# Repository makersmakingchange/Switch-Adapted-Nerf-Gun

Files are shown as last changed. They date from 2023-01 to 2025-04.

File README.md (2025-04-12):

# Switch Adapted Nerf Gun
The Switch Adapted Nerf Gun is designed to be a switch adapted toy for an older audience. The majority of switch adapted toys are designed for a younger audience, so this project aims to adapt a toy aimed at older children and make it switch accessible.

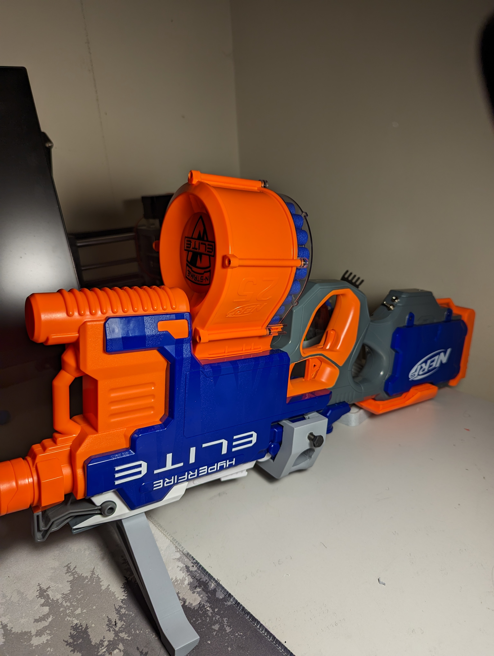
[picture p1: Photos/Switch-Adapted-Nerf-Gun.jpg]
Picture of Switch Adapted Nerf Gun.


## More info at
- [Makers Making Change Project Page](https://makersmakingchange.com/project/switch-adapted-nerf-gun/)

## How to Obtain a Switch Adapted Nerf Gun
### 1. Do it Yourself (DIY) or Do it Together (DIT)

This is an open-source assistive technology, so anyone is free to build it. All of the files and instructions required to build the Switch Adapted Nerf Gun are contained within this repository. Refer to the Maker Checklist below.

### 2. Request a build of this device

If you would like to obtain a Switch Adapted Nerf Gun, you may submit a build request through the [MMC Library Page](https://makersmakingchange.com/project/switch-adapted-nerf-gun/). The requestor is responsible for the cost of materials and any shipping.

### 3. How to build this device for someone else

If you have the skills and equipment to build this device, and would like to donate your time to create the switch for someone who needs it, visit the [MMC Maker Wanted](https://makersmakingchange.com/maker-wanted/) section.

## Getting Started

### 1. Read the Makers Checklist

The Makers Checklist contains a list of tasks to complete to build the device.
[The Makers Checklist](/Documentation/Switch_Adapted_Nerf_Gun_Maker_Checklist_V1.0.pdf)

### 2. Order the Off-The-Shelf Components

The [Bill of Materials](/Documentation/Switch_Adapted_Nerf_Gun_BOM_V1.0.xlsx) lists all of the parts and components required to build the Switch Adapted Nerf Gun. The main gun component needs to be ordered online. The rest of the off-the-shelf components are also online or may be available in smaller quantities at your local hardware store or dollar store.

### 3. Print the 3D Printable components

All of the files and individual print files can be in the [/Build_Files/3D_Printing_Files](/Build_Files/3D_Printing_Files/) folder.

### 4. Assemble the Switch Adapted Nerf Gun

Reference the [Assembly Guide](/Documentation/Switch_Adapted_Nerf_Gun_Assembly_Guide_V1.0.pdf) for the tools and steps required to build each portion.

## Files
### Documentation
| Document             | Version | Link |
|----------------------|---------|------|
| Design Rationale     | 1.0     | [Switch_Adapted_Nerf_Gun_Design_Rationale](/Documentation/Switch_Adapted_Nerf_Gun_Design_Rationale_V1.0.pdf)     |
| Maker Checklist      | 1.0     | [Switch_Adapted_Nerf_Gun_Maker_Checklist](/Documentation/Switch_Adapted_Nerf_Gun_Maker_Checklist_V1.0.pdf)     |
| Bill of Materials    | 1.0     | [Switch_Adapted_Nerf_Gun_Bill_of_Materials](/Documentation/Switch_Adapted_Nerf_Gun_BOM_V1.0.xlsx)     |
| 3D Printing Guide    | 1.0     | [Switch_Adapted_Nerf_Gun_3D_Printing_Guide](/Documentation/Switch_Adapted_Nerf_Gun_3D_Printing_Guide_V1.0.pdf)     |
| Assembly Guide       | 1.0     | [Switch_Adapted_Nerf_Gun_Assembly_Guide](/Documentation/Switch_Adapted_Nerf_Gun_Assembly_Guide_V1.0.pdf)     |
| User Guide           | 1.0     | [Switch_Adapted_Nerf_Gun_User_Guide](/Documentation/Switch_Adapted_Nerf_Gun_User_Guide_V1.0.pdf)    |
| Changelog            | 1.0     | [Switch_Adapted_Nerf_Gun_Changelog](/Documentation/Switch_Adapted_Nerf_Gun_Changelog_V1.0.pdf)     |

### Design Files
[CAD Files](/Design_Files/CAD_Files)

### Build Files
 - [3D Printing Files](/Build_Files/3D_Printing_Files)

## Attribution
Designers:
 - Design by [Nicholas Stallings](https://www.youtube.com/watch?v=sFg3B8Z95hU)
 - Documentation by Neil Squire Society/Makers Making Change

## License
Everything needed or used to design, make, test, or prepare the Switch Adapted Nerf Gun is licensed under the [Attribution-NonCommercial-ShareAlike 4.0 ](https://creativecommons.org/licenses/by-nc-sa/4.0/).

Accompanying material such as instruction manuals, videos, and other copyrightable works that are useful but not necessary to design, make, test, or prepare the <Device-Name> are published under a Creative Commons Attribution-ShareAlike 4.0 license https://creativecommons.org/licenses/by-sa/4.0/ (CC BY-SA 4.0).

---
<!-- ABOUT MMC START -->
## About Makers Making Change
[Makers Making Change Logo](https://www.makersmakingchange.com/)

Makers Making Change is a program of [Neil Squire](https://www.neilsquire.ca/), a Canadian non-profit that uses technology, knowledge, and passion to empower people with disabilities.

Makers Making Change leverages the capacity of community based Makers, Disability Professionals and Volunteers to develop and deliver affordable Open Source Assistive Technologies.

 - Website: [www.MakersMakingChange.com](https://www.makersmakingchange.com/)
 - GitHub: [makersmakingchange](https://github.com/makersmakingchange)
 - Bluesky: [@makersmakingchange.bsky.social](https://bsky.app/profile/makersmakingchange.bsky.social)
 - Instagram: [@makersmakingchange](https://www.instagram.com/makersmakingchange)
 - Facebook: [makersmakechange](https://www.facebook.com/makersmakechange)
 - LinkedIn: [Neil Squire Society](https://www.linkedin.com/company/neil-squire-society/)
 - Thingiverse: [makersmakingchange](https://www.thingiverse.com/makersmakingchange/about)
 - Printables: [MakersMakingChange](https://www.printables.com/@MakersMakingChange)

### Contact Us
For technical questions, to get involved, or to share your experience we encourage you to [visit our website](https://www.makersmakingchange.com/) or [contact us](https://www.makersmakingchange.com/s/contact).
<!-- ABOUT MMC END -->

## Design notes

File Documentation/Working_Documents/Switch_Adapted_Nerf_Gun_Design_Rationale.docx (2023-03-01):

# Introduction

The Switch Adapted Nerf Gun is designed to be a switch adapted toy for an older audience. The majority of switch adapted toys are designed for a younger audience, so this project aims to adapt a toy aimed at older users and make it switch accessible.

# Research

Commercial
Name | Image | Price | Link

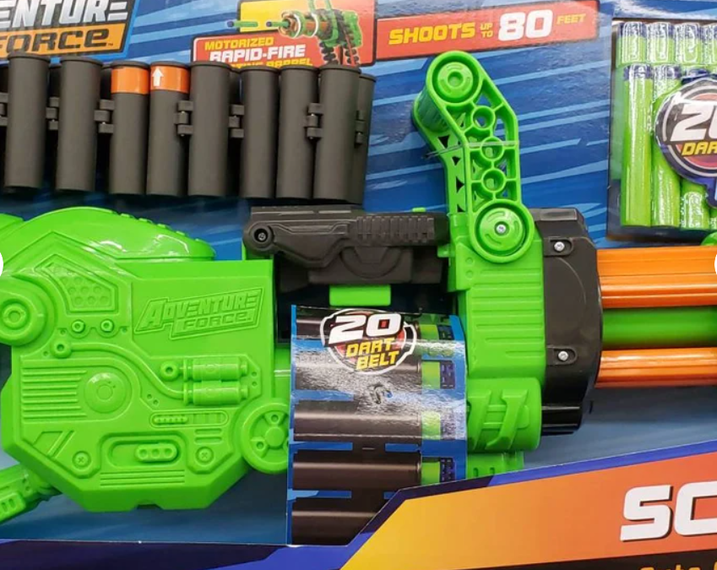
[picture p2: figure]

Switch Adapted modified Dart Blaster. For special needs. | | $99.74 | Link (https://www.etsy.com/ca/listing/648802112/switch-adapted-modified-dart-blaster-for)

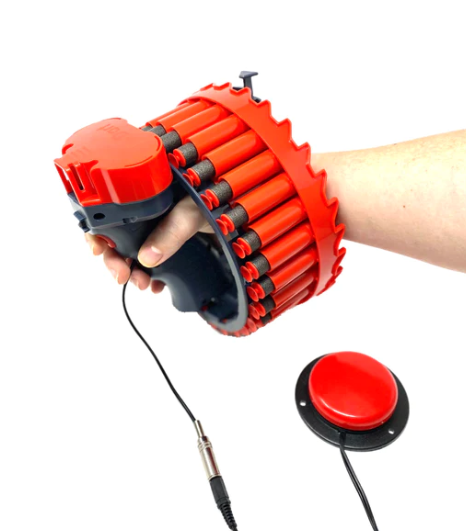
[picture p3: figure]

Dart Gun – Switch Adapted | | $70 | Link (https://adaptabilities.net/en-ca/products/switch-adapted-dart-gun-assistive-technology-toy-for-special-needs-education-occupational-physical-and-speech-therapy)

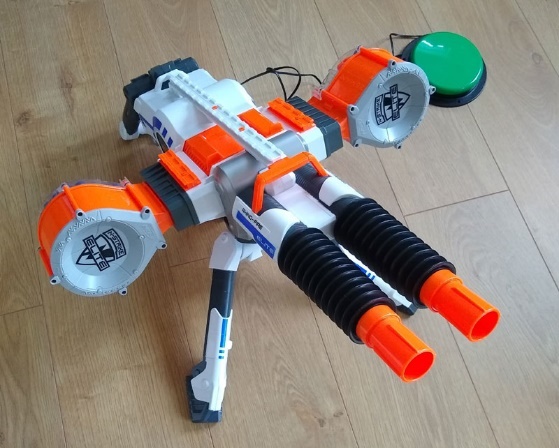
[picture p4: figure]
NERF Rhino switch adapted large plastic double-barrelled toy sentry gun.

Switch Adapted NERF Rhino-Fire Elite foam dart gun | | Price available upon email request | Link (https://oneswitch.org.uk/page/shop-switch-adapted-nerf-foam-dart-gun)

DIY
Name | Image | Price | Link

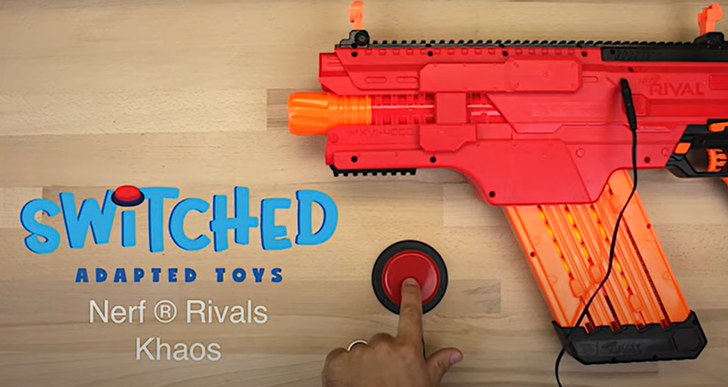
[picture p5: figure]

SWITCHED Adapted Toys - Nerf Rivals Khaos - Manual | | Unavailable | Link (https://www.switchedtoys.org/adapt-attack)

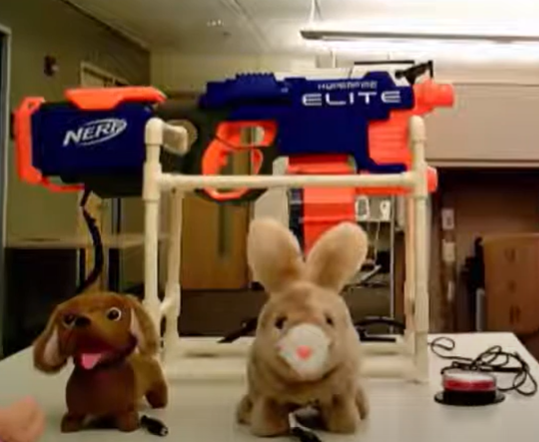
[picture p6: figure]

IATP- Switch adapted Nerf gun | | Unavailable | Link (https://www.youtube.com/watch?v=AM-woh1qSKs)

# Requirements

## Goals

G01 | Allow a Nerf gun to be operated by an accessible switch

## Functional Requirements

F01 | Add a mono jack to allow the primary user to control the feed motor
F02 | Add a toggle switch to allow the secondary user to toggle the flywheel motor
F03 | Add a stand that allows the gun to standalone on a surface and be mounted on a ¼-20 UNC system

## Non-functional Requirement

NF01 | Add a second mono jack to allow the primary user to operate the flywheel motor.

## Constraints

C01 | Design must still allow the gun to be used normally

# Prototyping

When opening the gun, the circuit was found to be different from the circuit in the gun in the tutorial video. Minor changes to the procedure had to be made to adapt the feed motor trigger. The initial circuit diagram can be seen on the left, while the modified circuit diagram is on the right.

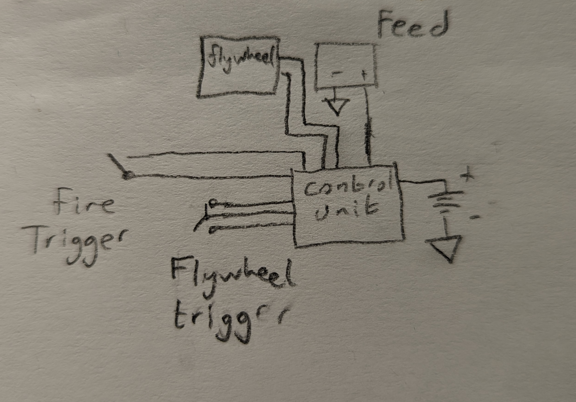
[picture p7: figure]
Original circuit diragram
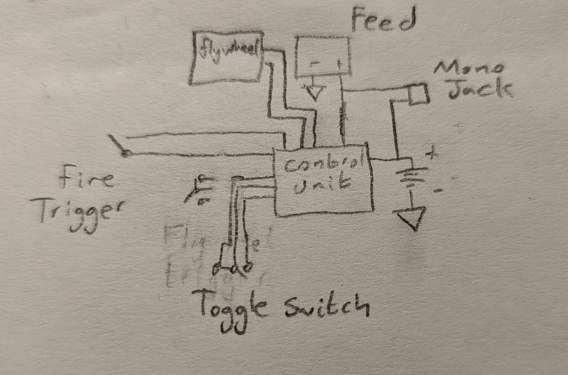
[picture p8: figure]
Modified circuit diagram

Two stands were designed for the gun. One bipod style desk stand was designed to fit over the attachment rail and allow the gun to stand upside down on a flat surface, while a ¼-20 bolt stand was developed that attaches to the gun near the centre of gravity and allows the gun to be attached to a standard ¼-20 mounting system.

# Testing

The successfully adapted toy was tested with a standard 3.5 mm switch using both the desk stand and the ¼-20 bolt stand. The gun was able to stand and support itself firing with both stands.

# Opportunities for Improvement

Once the control circuit is better understood, a 3.5 mm jack can be put in parallel with the toggle switch to make the flywheel motor usable by the primary user.

A system could be constructed to trigger both motors on the same switch, with a roughly one second delay on the feed motor to allow the firing motor to get up to speed.

© 2022 by Neil Squire. This work is licensed under the CC BY SA 4.0 License: http://creativecommons.org/licenses/by-sa/4.0 Files available at https://makersmakingchange.com/project/switch-adapted-nerf-gun/ Page 10 of 10

V1.0 | January 2023 Switch Adapted Nerf Gun Design Rationale

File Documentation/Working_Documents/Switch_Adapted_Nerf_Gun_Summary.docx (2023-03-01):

# Title

Switch Adapted Nerf Gun

## Subtitle

A Nerf Hyperfire Elite gun that has been adapted for use with a 3.5mm mono switch

## Device Details

### Overview

The Switch Adapted Nerf Gun is designed to be a switch adapted toy for an older audience. The majority of switch adapted toys are designed for a younger audience, so this project aims to adapt a toy aimed at older users and make it switch accessible.

### Usage

To set up the Nerf gun on a flat surface, take the Desk stand and slide it onto the top attachment rail. This will allow the gun to stand by itself upside down.

To set up the Nerf gun on a ¼-20 bolt system, take the bolt stand and attach it to the section of the gun above the trigger as seen in the assembly guide. This will allow the gun to be attached to any ¼-20 mount system.

To use the gun, a 3.5mm switch can be plugged into the jack, and a secondary user can flick the toggle switch to activate the flywheel motors. Once the motors are spinning, the switch can be pressed and held to activate the feed motor for as long as the button is held.

### Cost

~$95 total

~$75 toy

~$20 dollars batteries and adaptation

### Build Instructions

The build involves opening the nerf gun to modify two switches that will allow the gun to be fired with a 3.5mm mono switch.

#### Skills Required

- Soldering
- 3D printing

#### Time Required

3D Printing:

8h38min

Assembly:

1h30min

#### Tools

Soldering Iron

Screwdriver

Wire Strippers

Drill with 1/4inch drill bit

#### Components

- Nerf Hyperfire Elite
- D-Cell Batteries
- ¼ -20 T-Slot Nut
- ¼-20 Bolts

#### 3D Printing

- Desk Stand
- Bolt Stand

### Attribution

- Switch adaptation design by Nicholas Stallings (https://www.youtube.com/watch?v=sFg3B8Z95hU)
- Mounting options design by Neil Squire Society/Makers Making Change
- Documentation by Neil Squire Society/Makers Making Change

© 2022 by Neil Squire. This work is licensed under the CC BY SA 4.0 License: http://creativecommons.org/licenses/by-sa/4.0 Files available at https://makersmakingchange.com/project/switch-adapted-nerf-gun/ Page 10 of 10

V1.0 | January 2023 Switch Adapted Nerf Gun Summary

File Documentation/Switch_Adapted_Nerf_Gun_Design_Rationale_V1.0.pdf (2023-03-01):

V1.0 | January 2023

## Switch Adapted Nerf Gun

## DESIGN RATIONALE

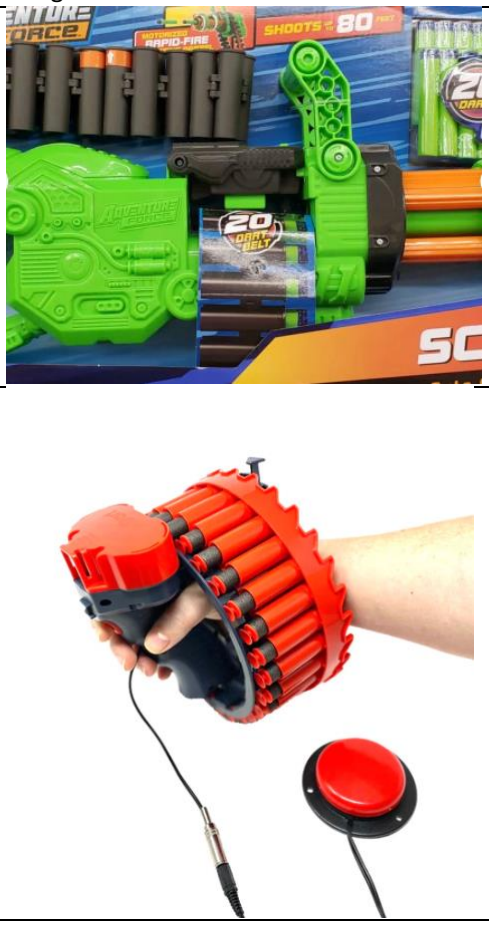
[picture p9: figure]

© 2022 by Neil Squire. (https://neilsquire.ca/)
This work is licensed under the CC BY SA 4.0 License: http://creativecommons.org/licenses/by-sa/4.0
Files available at https://makersmakingchange.com/project/switch-adapted-nerf-gun/ | Page 1 of 4

### Introduction

The Switch Adapted Nerf Gun is designed to be a switch adapted toy for an older audience. The majority of switch adapted toys are designed for a younger audience, so this project aims to adapt a toy aimed at older users and make it switch accessible.

### Research

Commercial
Name | Image | Price | Link
Switch Adapted modified Dart Blaster. For special needs. | | $99.74 | Link (https://www.etsy.com/ca/listing/648802112/switch-adapted-modified-dart-blaster-for)
Dart Gun – Switch Adapted | | $70 | Link (https://adaptabilities.net/en-ca/products/switch-adapted-dart-gun-assistive-technology-toy-for-special-needs-education-occupational-physical-and-speech-therapy)

## DESIGN RATIONALE

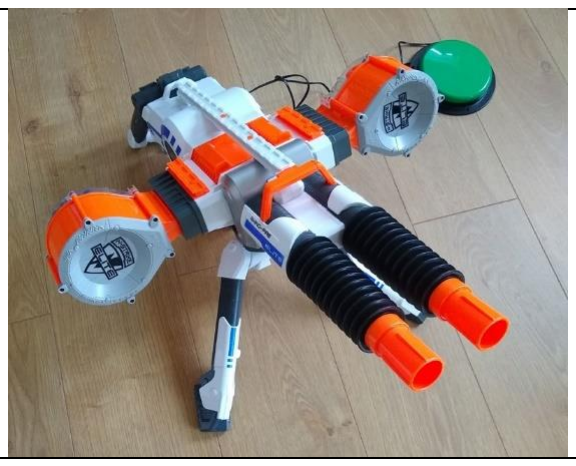
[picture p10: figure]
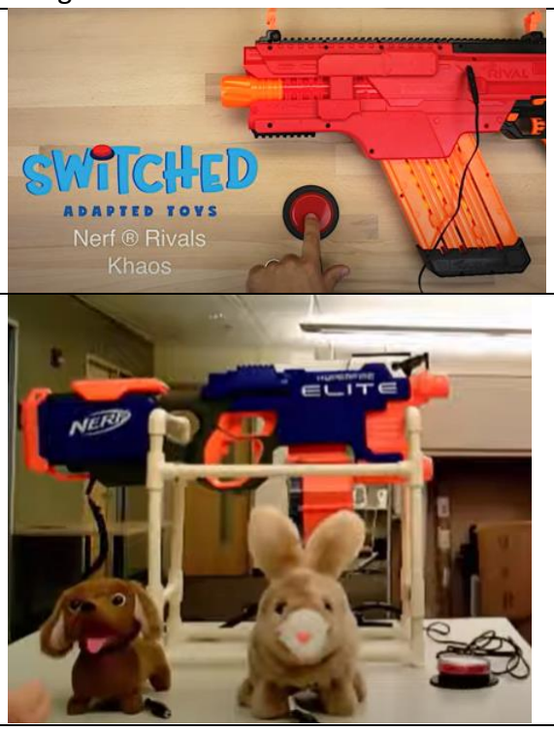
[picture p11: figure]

Files available at https://makersmakingchange.com/project/switch-adapted-nerf-gun/ | Page 2 of 4

Switch
Adapted NERF
Rhino-Fire Elite
foam dart gun

Price available
upon email
request

Link (https://oneswitch.org.uk/page/shop-switch-adapted-nerf-foam-dart-gun)

DIY
Name | Image | Price | Link
SWITCHED Adapted Toys -Nerf Rivals Khaos -Manual | | Unavailable | Link (https://www.switchedtoys.org/adapt-attack)
IATP- Switch adapted Nerf gun | | Unavailable | Link (https://www.youtube.com/watch?v=AM-woh1qSKs)

### Requirements

### Goals

G01 Allow a Nerf gun to be operated by an accessible switch

### Functional Requirements

F01 | Add a mono jack to allow the primary user to control the feed motor
F02 | Add a toggle switch to allow the secondary user to toggle the flywheel motor
F03 | Add a stand that allows the gun to standalone on a surface and be mounted on a ¼-20 UNC system

## DESIGN RATIONALE

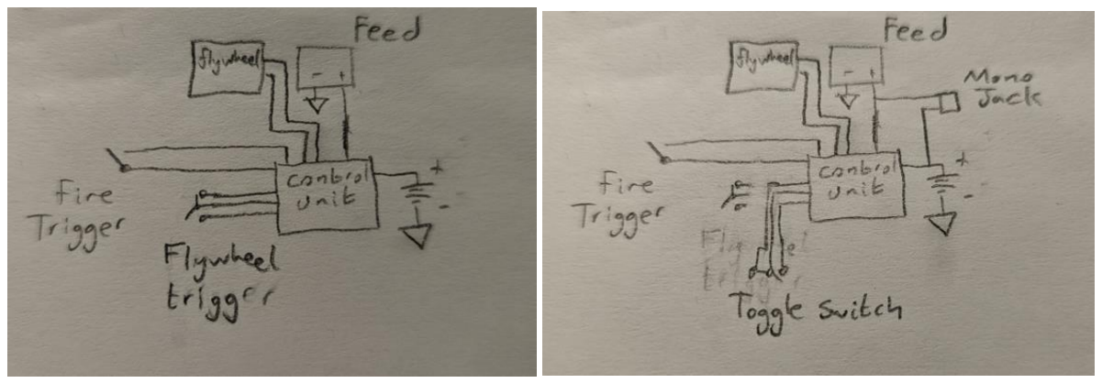
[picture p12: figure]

Files available at https://makersmakingchange.com/project/switch-adapted-nerf-gun/ | Page 3 of 4

### Non-functional Requirement

NF01 Add a second mono jack to allow the primary user to operate the flywheel motor.

### Constraints

C01 Design must still allow the gun to be used normally

### Prototyping

When opening the gun, the circuit was found to be different from the circuit in the gun in the tutorial video. Minor changes to the procedure had to be made to adapt the feed motor trigger. The initial circuit diagram can be seen on the left, while the modified circuit diagram is on the right.

Two stands were designed for the gun. One bipod style desk stand was designed to fit over the attachment rail and allow the gun to stand upside down on a flat surface, while a ¼-20 bolt stand was developed that attaches to the gun near the centre of gravity and allows the gun to be attached to a standard ¼-20 mounting system.

### Testing

The successfully adapted toy was tested with a standard 3.5 mm switch using both the desk stand and the ¼-20 bolt stand. The gun was able to stand and support itself firing with both stands.

### Opportunities for Improvement

Once the control circuit is better understood, a 3.5 mm jack can be put in parallel with the toggle switch to make the flywheel motor usable by the primary user.

## DESIGN RATIONALE

Files available at https://makersmakingchange.com/project/switch-adapted-nerf-gun/ | Page 4 of 4

A system could be constructed to trigger both motors on the same switch, with a roughly one second delay on the feed motor to allow the firing motor to get up to speed.

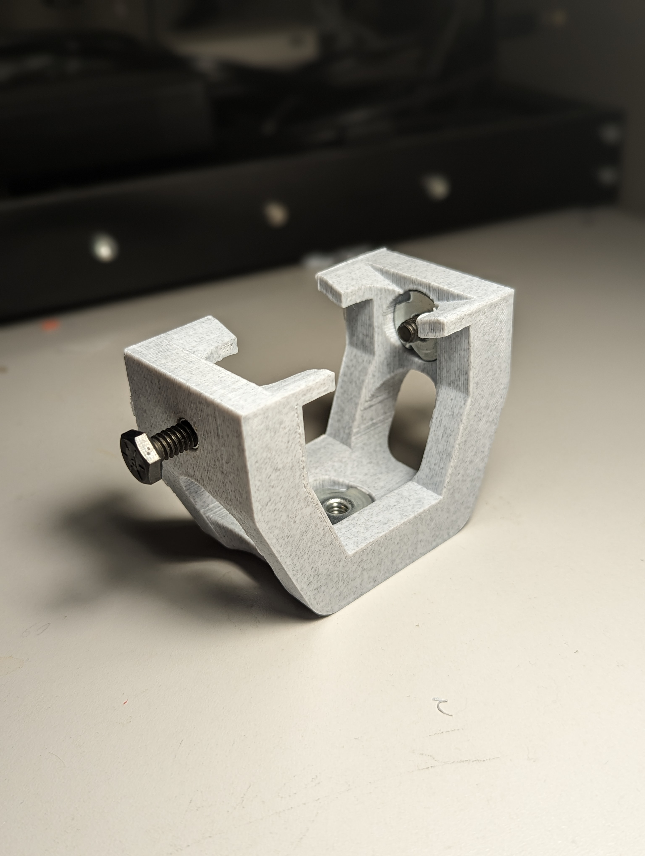
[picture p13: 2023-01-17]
Photos/PXL_20230106_003917938.PORTRAIT.jpg

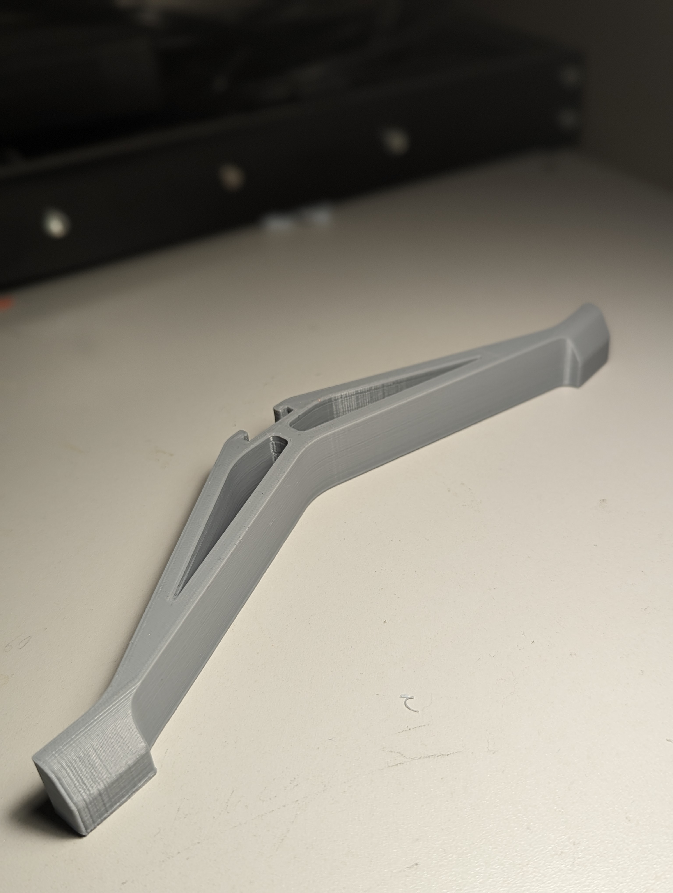
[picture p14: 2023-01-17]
Photos/PXL_20230106_003909670.PORTRAIT.jpg

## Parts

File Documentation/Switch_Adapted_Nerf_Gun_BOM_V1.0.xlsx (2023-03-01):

Device: Switch Adapted Nerf Gun |  | Total Cost | Total Print time (hr) | Total filament (g)
Version: V1.0 | Date Created: 01/06/2023 | $91.19 | 8.63 | 64
Commercial Parts:
Part type (Electrical. Mechanical, Sanitization, ect) | Part Name | Quantity Needed | Pkg Quantity | Price per package | Price per Unit | Price for qty needed | Link
Mechanical | Nerf N-Strike Elite HyperFire Blaseter | 1 | 1 | $71.99 | $71.99 | $71.99 | https://www.amazon.ca/dp/B018KLHT5O
Electrical | D Cell Battery | 4 | 4 | $12.82 | $3.21 | $12.82 | https://www.amazon.ca/dp/B00000JHQC/
Mechanical | 1/4-20 T Nut | 3 | 100 | $14.40 | $0.14 | $0.43 | https://www.mcmaster.com/90975A309/
Mechanical | 1/4-20 Bolt | 2 | 25 | $17.99 | $0.72 | $1.44 | https://www.amazon.ca/dp/B097NWWQFC/
Electrical | Toggle Switch | 1 | 10 | $15.96 | $1.60 | $1.60 | https://www.amazon.ca/dp/B01BWL7Z44/ | https://www.aliexpress.com/item/1005001558947112.html
Electrical | Mono Jack | 1 | 10 | $13.09 | $1.31 | $1.31 | https://www.amazon.ca/dp/B07R9SV6F5/
3D Printed Parts ESTIMATED PRICING USING 1KG ROLL COST: | $25.00
Part | Description | Quantity Needed | TOTAL Mass (g) | Estimated Price | Print Time (Min) | Link
Desk Stand | Allows the gun to stand unsupported on a surface | 1 | 27 | $0.68 | 232
Bolt Stand | Allows the gun to be attacked to a 1/4-20 system | 1 | 37 | $0.92 | 286
 |  |  |  | $0.00
 |  |  |  | $0.00
 |  |  |  | $0.00
 |  |  | Total Print Cost: | $1.60
Tools for Assembly
Alternatives (if there are other sources for some parts link them below)
Part and description | Link

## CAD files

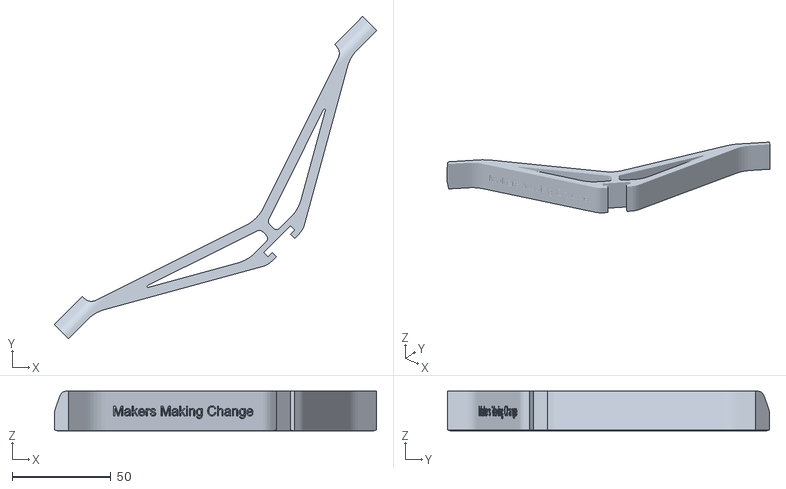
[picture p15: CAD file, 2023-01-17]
Build_Files/3D_Printing_Files/Desk_Stand.stl
162.6 x 162.6 x 20.0

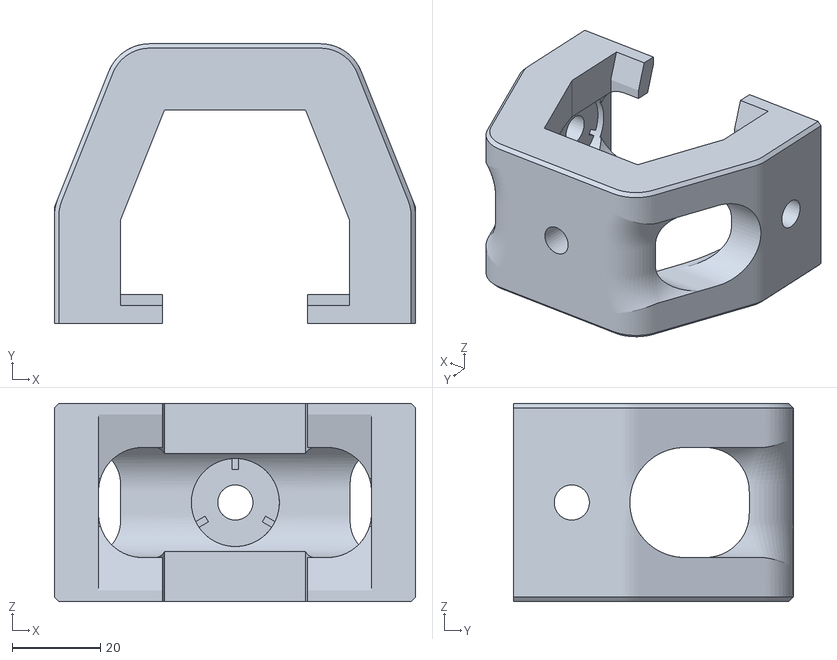
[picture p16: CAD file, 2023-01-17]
Build_Files/3D_Printing_Files/Bolt_Stand.stl
82.0 x 63.5 x 45.0

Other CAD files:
Design_Files/CAD_Files/Bolt Stand v6.f3d
Design_Files/CAD_Files/Stand v3.f3d

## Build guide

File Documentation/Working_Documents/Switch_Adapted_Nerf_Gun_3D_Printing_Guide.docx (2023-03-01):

# 3D Printing Summary

Metrics | Desk Stand | Bolt Stand
Total Print Time (min) | 232 | 286
Total Number of Components | 1 | 1
Typical Total Mass (g) | 27 | 37
Typical Number of Print Setups | 1 | 1

# 3D Printing Settings

Print File Name | Qty | Total Print Time (hr:min) | Mass (g) | Infill (%) | Support(Y/N) | Layer Height/ Nozzle Diameter(mm) | Notes (orientation, special settings, etc.)
Desk_Stand.stl | 1 | 3:52 | 27 | 20 | N | 0.2/0.4 | - Print in default stl orientation
Bolt_Stand.stl | 1 | 4:46 | 37 | 20 | N | 0.2/0.4 | - Print in default stl orientation

# Customization Options

- The device can be printed in any colour the user wants

# Post-Processing

- Use a hobby knife to remove any sharp edges.
- If using the bolt stand, insert ¼-20 t-nuts into the three slots in the Bolt stand as seen in the assembly guide.

# Examples of Quality Prints

Photos of Desk Stand

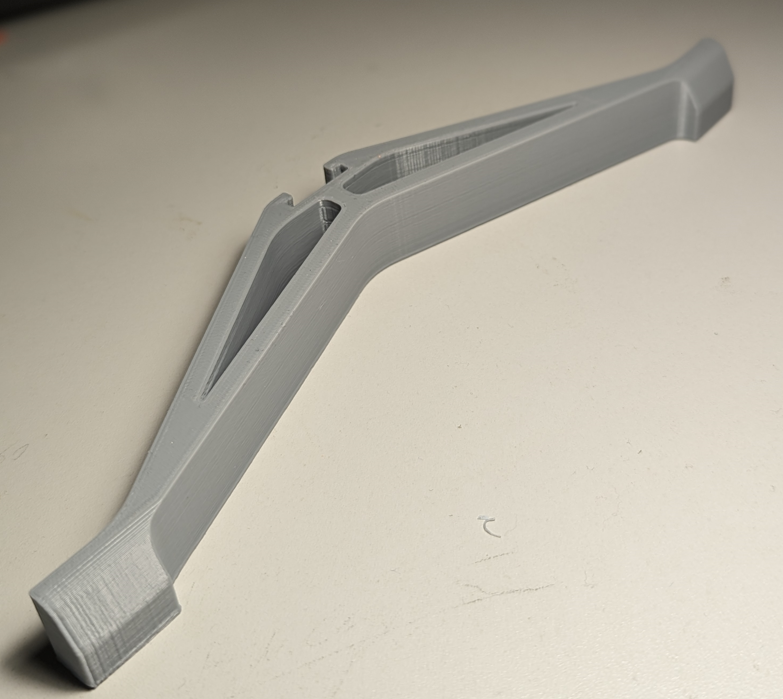
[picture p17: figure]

Photos of Bolt Stand

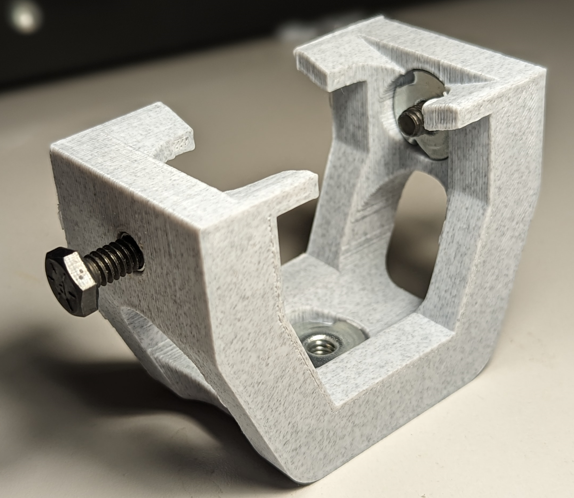
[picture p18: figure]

© 2022 by Neil Squire Society This work is licensed under the CC BY SA 4.0 License: http://creativecommons.org/licenses/by-sa/4.0 Files available at https://makersmakingchange.com/project/switch-adapted-nerf-gun/ Page 10 of 10

V1.0 | January 2023 Switch Adapted Nerf Gun 3D Printing Guide

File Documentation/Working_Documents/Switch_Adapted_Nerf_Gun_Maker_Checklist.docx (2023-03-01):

# Maker To Do List

- Read through the Assembly Guide to become familiar with required components, tools, supplies, and safety gear and overall assembly steps.
- Talk to User about customization options (e.g., color, any special requests, etc.)
- Order hardware components
- Gather tools, supplies, and safety equipment.
- Assemble the device
- Test device
- Print “User Quick Guide”

# Items to Give to User

- Assembled, tested device
- “User Quick Guide”

© 2022 by Neil Squire. This work is licensed under the CC BY SA 4.0 License: http://creativecommons.org/licenses/by-sa/4.0 Files available at https://makersmakingchange.com/project/switch-adapted-nerf-gun/ Page 10 of 10

V1.0 | January 2023 Switch Adapted Nerf Gun Maker Checklist

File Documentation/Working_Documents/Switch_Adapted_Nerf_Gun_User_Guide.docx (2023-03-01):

## Introduction

The Switch Adapted Nerf Gun is designed to be a switch adapted toy for an older audience. The majority of switch adapted toys are designed for a younger audience, so this project aims to adapt a toy aimed at older users and make it switch accessible.

## Features

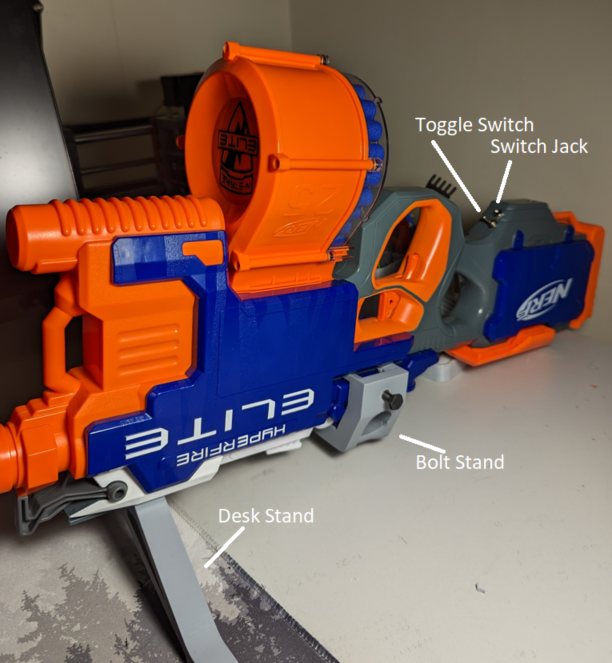
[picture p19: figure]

## Usage

To set up the Nerf gun on a flat surface, take the Desk stand and slide it onto the top attachment rail. This will allow the gun to stand by itself upside down.

To set up the Nerf gun on a ¼-20 bolt system, take the bolt stand and attach it to the section of the gun above the trigger as seen below. This will allow the gun to be attached to any ¼-20 mount system.

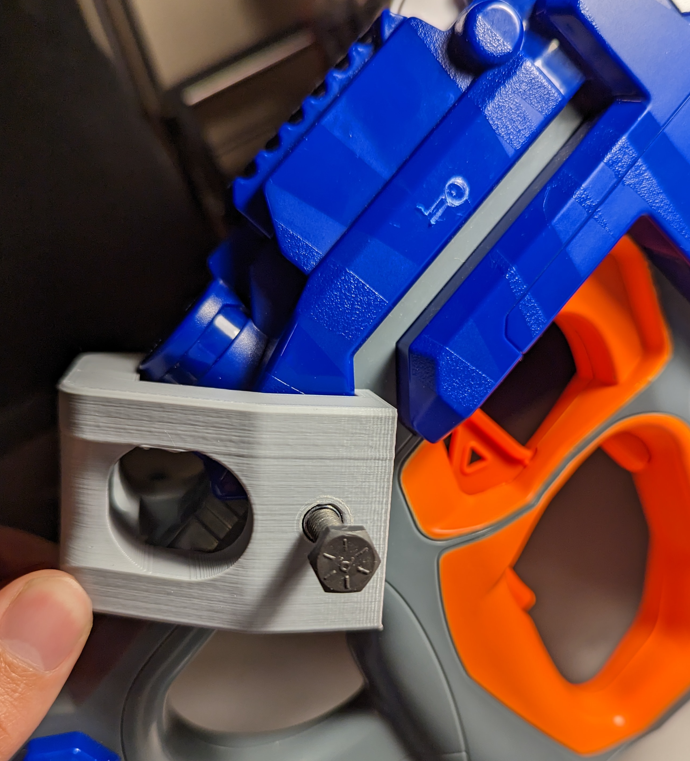
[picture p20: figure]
Bolt stand initially placed on gun
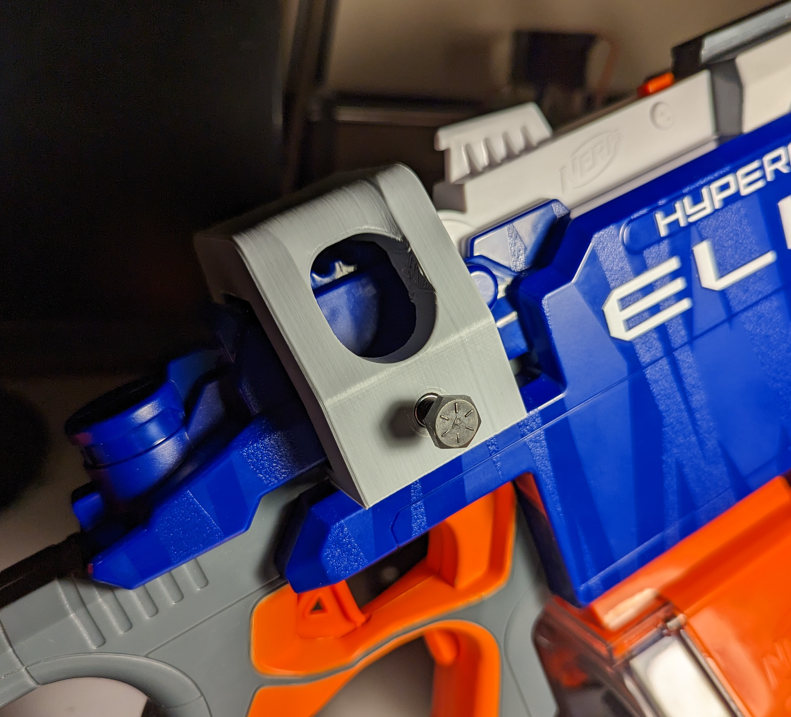
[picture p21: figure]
Bolt stand fully on gun

To use the gun, a 3.5mm switch can be plugged into the jack, and a secondary user can flick the toggle switch to activate the flywheel motors. Once the motors are spinning, the switch can be pressed and held to activate the feed motor for as long as the button is held.

## Compatibility

The device is compatible with standard 3.5mm switches as well as Nerf Elite darts.

## Cleaning

The device can be wiped clean with a damp cloth

© 2022 by Neil Squire. This work is licensed under the CC BY SA 4.0 License: http://creativecommons.org/licenses/by-sa/4.0 Files available at https://makersmakingchange.com/project/switch-adapted-nerf-gun/ Page 10 of 10

V1.0 | January 2023 Switch Adapted Nerf Gun user Quick Guide

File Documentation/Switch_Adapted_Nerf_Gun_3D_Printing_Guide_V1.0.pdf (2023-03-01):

V1.0 | January 2023

## Switch Adapted Nerf Gun

## 3D PRINTING GUIDE

© 2022 by Neil Squire Society This work is licensed under the CC BY SA 4.0 License: http://creativecommons.org/licenses/by-sa/4.0
Files available at https://makersmakingchange.com/project/switch-adapted-nerf-gun/ | Page 1 of 2

### 3D Printing Summary

Metrics | Desk Stand | Bolt Stand
Total Print Time (min) | 232 | 286
Total Number of Components | 1 | 1
Typical Total Mass (g) | 27 | 37
Typical Number of Print Setups | 1 | 1

### 3D Printing Settings

Print File Name | Qty | Total Print Time (hr:min) | Mass (g) | Infill (%) | Support(Y/N) | Layer Height/ Nozzle Diameter(mm) | Notes (orientation, special settings, etc.)
Desk_Stand.stl | 1 | 3:52 | 27 | 20 | N | 0.2/0.4 | -Print in default stl orientation
Bolt_Stand.stl | 1 | 4:46 | 37 | 20 | N | 0.2/0.4 | -Print in default stl orientation

### Customization Options

- The device can be printed in any colour the user wants

### Post-Processing

- Use a hobby knife to remove any sharp edges.
- If using the bolt stand, insert ¼-20 t-nuts into the three slots in the Bolt stand as seen in the assembly guide.

V1.0 | January 2023

## Switch Adapted Nerf Gun

## 3D PRINTING GUIDE

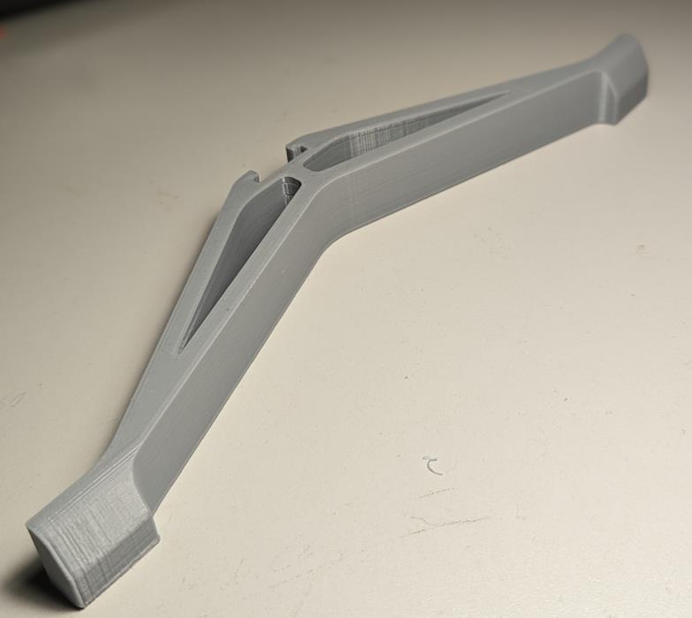
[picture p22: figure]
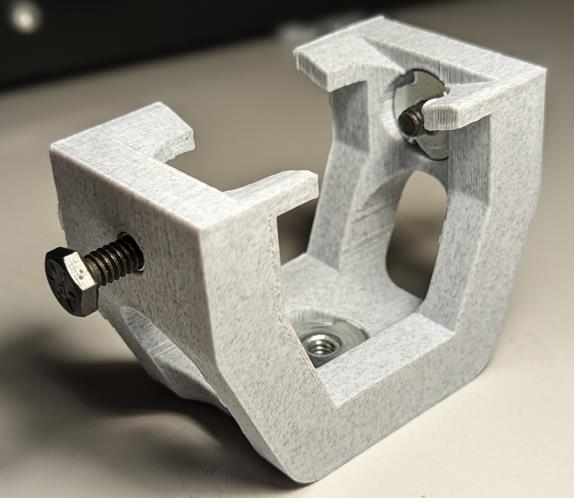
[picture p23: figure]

© 2022 by Neil Squire Society This work is licensed under the CC BY SA 4.0 License: http://creativecommons.org/licenses/by-sa/4.0
Files available at https://makersmakingchange.com/project/switch-adapted-nerf-gun/ | Page 2 of 2

### Examples of Quality Prints

Photos of Desk Stand

Photos of Bolt Stand

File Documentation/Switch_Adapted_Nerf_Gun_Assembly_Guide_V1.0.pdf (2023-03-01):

V1.0 | January 2023

# Switch Adapted Nerf Gun

# ASSEMBLY GUIDE

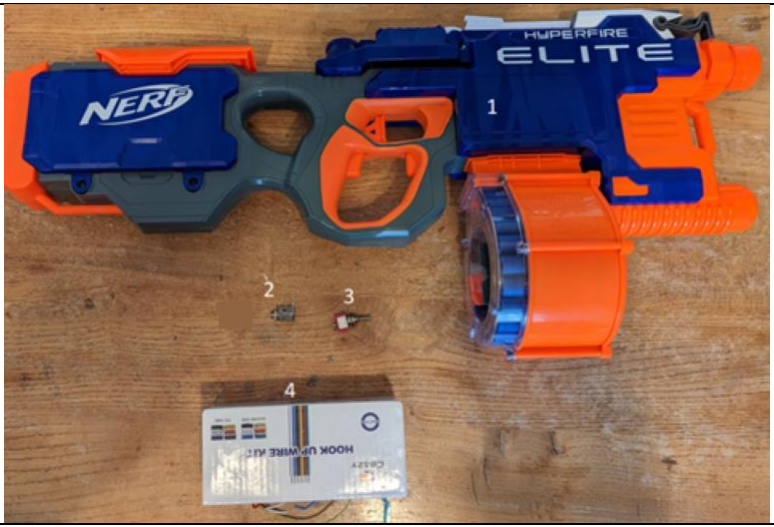
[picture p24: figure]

© 2022 by Neil Squire. (https://neilsquire.ca/)
This work is licensed under the CC BY SA 4.0 License: http://creativecommons.org/licenses/by-sa/4.0
Files available at https://makersmakingchange.com/project/switch-adapted-nerf-gun/ | Page 1 of 10

# Required Components

## BOM 1. 1x Nerf Hyperfire Elite 2. 1x Mono Jack 3. 1x Toggle Switch 4. Wire

# Required Tools

## - Soldering Iron - Solder - Electrical Tape - Wire Strippers - Screwdriver - Drill with ¼ inch bit

# ASSEMBLY GUIDE

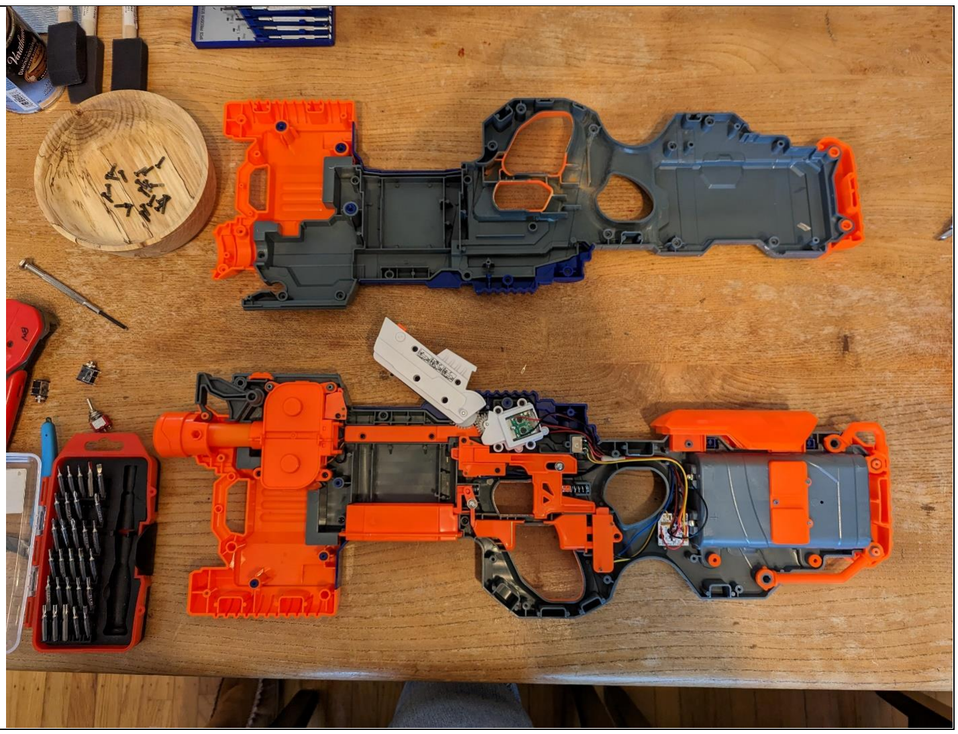
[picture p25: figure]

Files available at https://makersmakingchange.com/project/switch-adapted-nerf-gun/ | Page 2 of 10

# Required Personal Protective Equipment (PPE)

## - Eye Protection

# Assembly Instructions

## Step 1

## Remove all screw holding the two halves of the gun together and separate the gun into two

halves.

# ASSEMBLY GUIDE

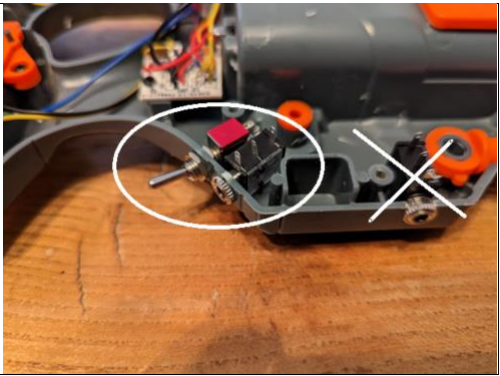
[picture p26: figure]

Files available at https://makersmakingchange.com/project/switch-adapted-nerf-gun/ | Page 3 of 10

## Step 2

Drill two quarter inch holes in the side of the shell with all the electronics. Test fit the toggle

## switch and mono jack before and after drilling to make sure there is enough space. Remove

both after testing. (While the below photo has two mono jacks, only one was used in the final product) The location of the holes is not important, ifthere is room to route the wires from the jacks.

# ASSEMBLY GUIDE

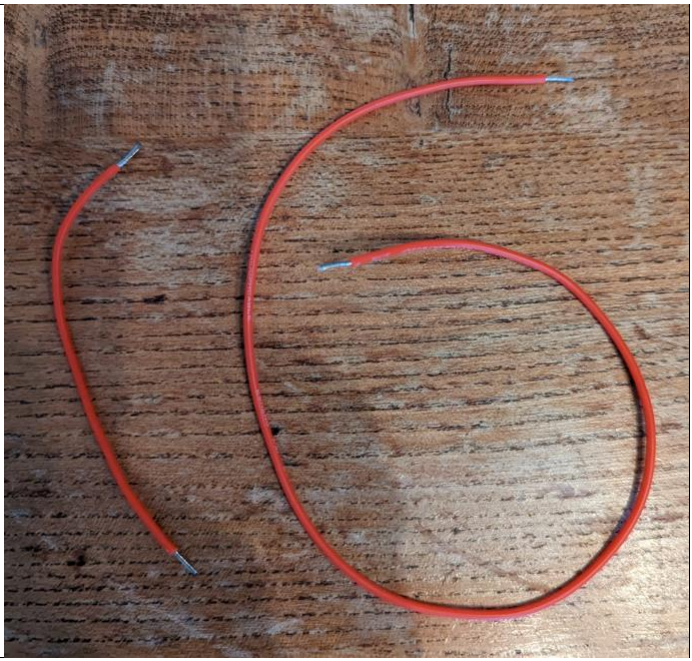
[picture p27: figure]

Files available at https://makersmakingchange.com/project/switch-adapted-nerf-gun/ | Page 4 of 10

## Step 3

Cut two lengths of wire. The lengths of the wires will change depending on where you put the mono jack. One length should be long enough to reach the positive terminal of the battery from the mono jack, the other should reach from the mono jack to the exposed circuit board on the white plastic. Strip both ends of each wire.

## Step 4

Take the longer wire, and solder one end to the pin on the mono jack closest to the plug, and the other end on the red wire on the feed motor circuit board (in the top left of the picture). Take the shorter wire

# ASSEMBLY GUIDE

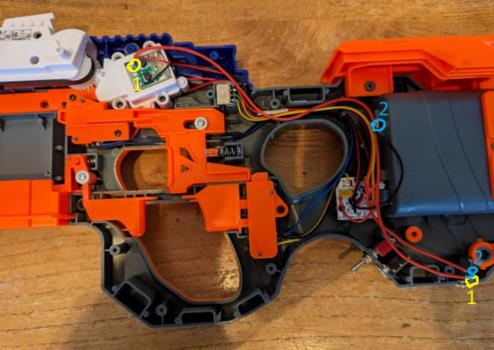
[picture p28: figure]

Files available at https://makersmakingchange.com/project/switch-adapted-nerf-gun/ | Page 5 of 10

and connect one end to the red wire on the battery pack and the other to the middle pin on the mono jack.

# ASSEMBLY GUIDE

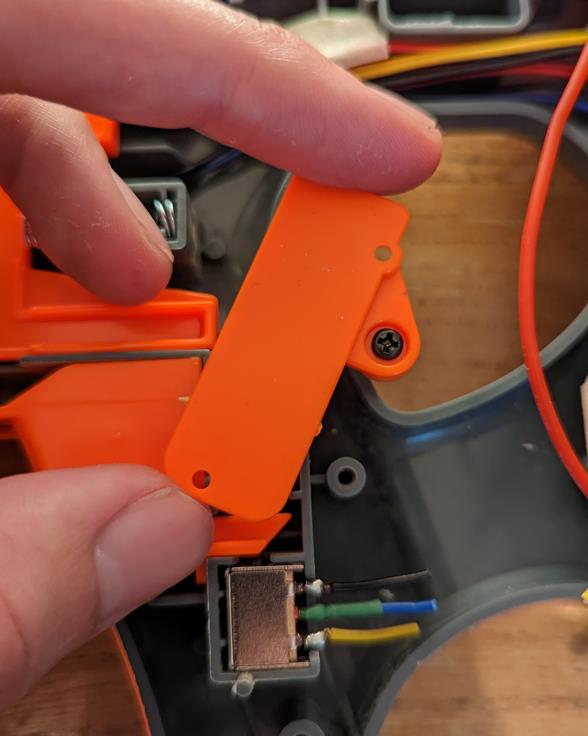
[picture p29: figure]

Files available at https://makersmakingchange.com/project/switch-adapted-nerf-gun/ | Page 6 of 10

## Step 5

Remove the orange cover from over the flywheel trigger sensor.

# ASSEMBLY GUIDE

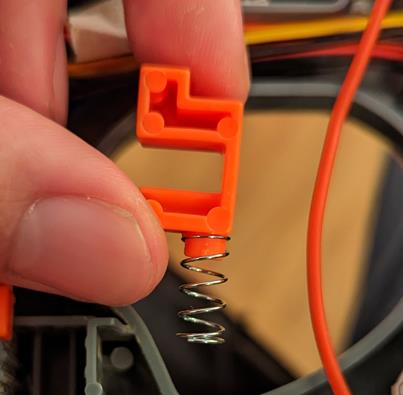
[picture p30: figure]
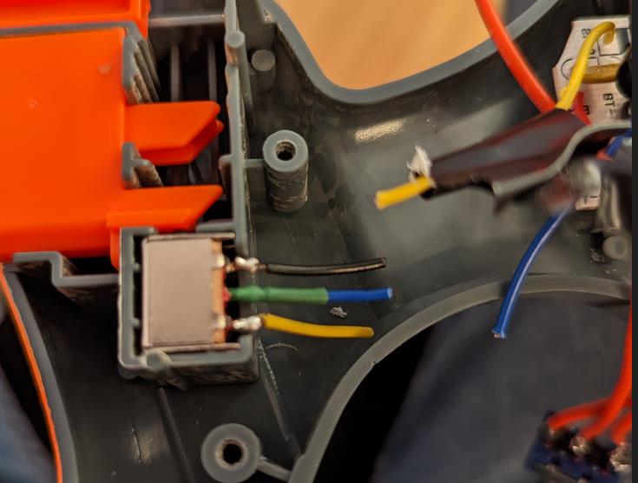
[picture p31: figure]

Files available at https://makersmakingchange.com/project/switch-adapted-nerf-gun/ | Page 7 of 10

## Step 6

Remove the C-shaped piece of plastic with the spring attached and discard. Replace the cover over the sensor.

## Step 7

Cut the three wires connected to the flywheel trigger sensor. This will render the original trigger inoperable.

# ASSEMBLY GUIDE

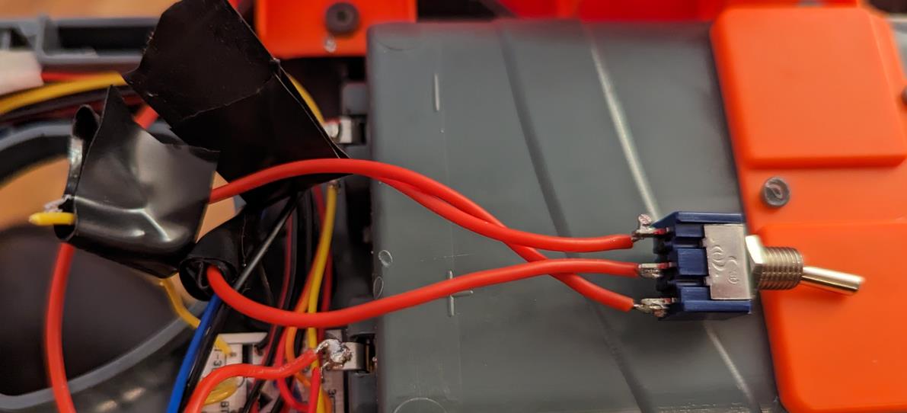
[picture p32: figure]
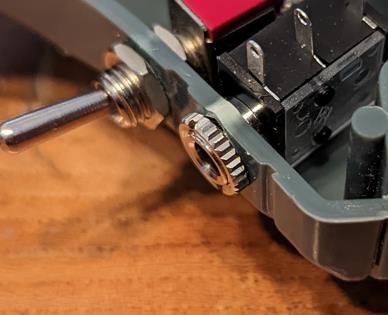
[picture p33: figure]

Files available at https://makersmakingchange.com/project/switch-adapted-nerf-gun/ | Page 8 of 10

## Step 8

Connect the wires that have just been cut to a three-pin toggle switch. Connect the middle wire to the centre pin of the toggle switch, with the other wires on either side. Depending on where you drilled your hole for the toggle switch, you may need to cut several lengths of wire to extend the original wires to reach the toggle switch.

## Step 9

Install both the toggle switch and the mono jack into the holes drilled into the housing. Secure them with the locking nuts they came with. Route all the wires with the existing wires to keep

## them from any pinch zones

# ASSEMBLY GUIDE

## Step 10

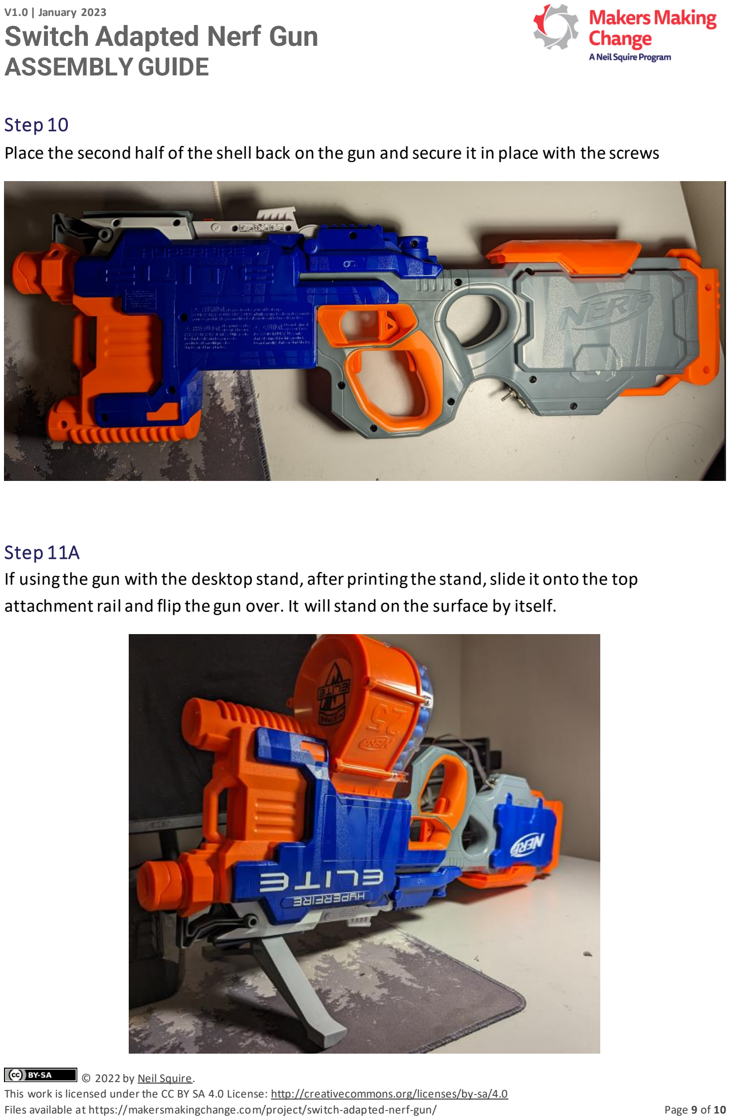
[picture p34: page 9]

Files available at https://makersmakingchange.com/project/switch-adapted-nerf-gun/ | Page 9 of 10

## Place the second half of the shell back on the gun and secure it in place with the screws

## Step 11A

## If using the gun with the desktop stand, after printing the stand, slide it onto the top

attachment rail and flip the gun over. It will stand on the surface by itself.

# ASSEMBLY GUIDE

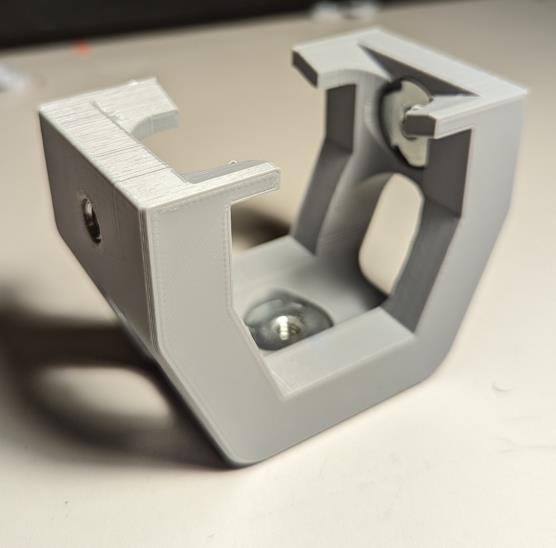
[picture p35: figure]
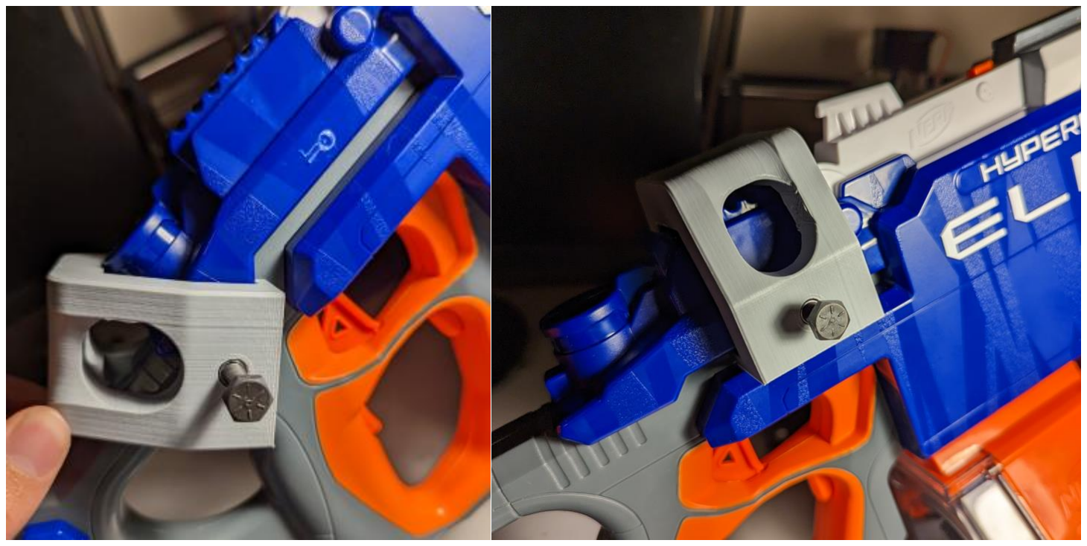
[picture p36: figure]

Files available at https://makersmakingchange.com/project/switch-adapted-nerf-gun/ | Page 10 of 10

## Step 11B

If using the Nerf gun with the bolt stand, after printing the stand, take 3 t-nuts and gently press

## them into the slots on the printed part. Use a bolt and tighten the nuts into position

## Step 12B

Attach two bolts to the side two nuts. Slide the assembly over the top section of the gun above the trigger as seen in the photos. When the stand is in place, tighten the two bolts to lock it in place. The nut on the bottom can be used to attach the gun to any ¼ - 20 bolt system.
